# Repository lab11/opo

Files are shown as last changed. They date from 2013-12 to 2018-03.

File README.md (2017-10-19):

Opo
===

Opo is a face-to-face interaction sensor, able to characterize face to face interactions with 5~cm accuracy 
and 2~s temporal fidelity while maintaining a week-long battery life on a relatively small (110 mAh) battery.

Installation
---

1) Checkout my version of Contiki:

    git clone --recursive https://github.com/lab11/contiki.git
    git checkout cc2538-opo

2) Install a toolchain:
    Detailed instructions can be found at https://github.com/lab11/contiki/tree/cc2538-opo/platform/cc2538dk
    In ubuntu:
    sudo add-apt-repository ppa:terry.guo/gcc-arm-embedded
    sudo apt-get update
    sudo pat-get install gcc-arm-none-eabi 

3) Checkout the Opo repo
    git clone https://github.com/lab11/opo.git

4) Download Android studio 
    http://developer.android.com/sdk/index.html

5) Either make or ask us for a programmer
    https://github.com/lab11/epic-multi-prog.git

6) Either make or ask us for Opo boards
    opo/hardware/Opo8001v2 - No FTDI

7) If making your own boards, we recommend these batteries: https://www.sparkfun.com/products/13112

8) Go to /contiki/apps/opo8001v2opo_plugin in the Opo repo.

9) Modify line 9 (CONTIKI = /home/wwhuang/Dropbox/git/contiki) to point to whever you checked out my Contiki repo to (step 1). 

10) Connect the Opo to the programmer using a tag connect cable <http://www.tag-connect.com/TC2030-IDC-NL>. 

11) Install the opo89001v2opo_plugin app by typing python2 idmake ID in a terminal, where ID is a 16 bit unsigned integer 
that will be used as the targeted Opo's ID during ranging operations.

Usage
---

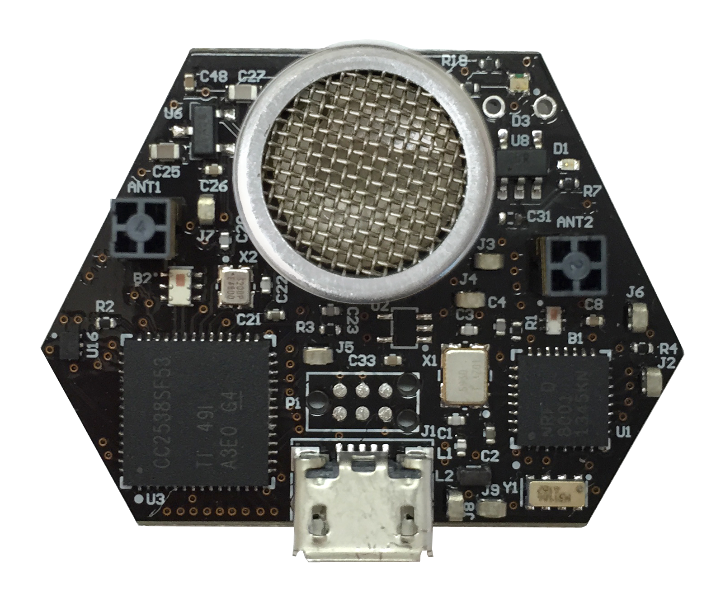
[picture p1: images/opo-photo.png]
Opo sensor


### Attaching Opos to people

We are currently working on a 3d printed case. In the meantime, obtain a lanyward, such as this one 
<https://www.amazon.com/MIFFLIN-Vertical-Badge-Holder-Lanyard/dp/B01G7VTE98/ref=sr_1_2?ie=UTF8&qid=1499377440&sr=8-2-spons&keywords=lanyard&psc=1&smid=A29P802DGSGI7W>.
Carve a hole in the plastic such that the transducer (large silver part with mesh) pokes out of the sheathe, and use 
electric tape to secure the Opo inside the sheathe if neccessary. 

The Opo must be worn such that they are unobstructed (e.g, NOT behind a shirt), and so that the transducer is facing 
forward. Ideally, the Opo should be worn near the neck, such that they are facing forward while not pointing upwards, 
as can happen on the chest.

### Charging the Opos and downloading the data

Opos can be charged from standard microUSB chargers, such as the ones used to charge smartphones. They can also 
be charged from laptops, or really anything that provides USB power. 

To download the data, one must plug in the Opo and then run the nodejs application, cloudcomm.js, found in the 
/node folder of the Opo repository. When the Opo is plugged in, the LED should turn blue, and when the Opo is uploading data the blue and red LEDs will blink. Keep in mind the LEDs are provided by one RGB LED, so if both the red and blue LEDs are on, the light will look purple. The data gets downloaded as JSON in a file titled opo_cc_data.dat. The key pieces of data are: 

* RX_ID: This Opo's ID 
* TX_ID: The other Opo's ID
* RANGE: distance between the two Opos in meters 
* M_UNIXTIME: This Opo's sense of what time the interaction occurred, expressed as a unix timestamp. 
* TX_UNIXTIME: The other Opo's sense of what time the interaction occurred, expressed as a unix timestamp.

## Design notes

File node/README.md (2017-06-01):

Cloudcomm
========

1. Install the most recent release of nodejs
	- https://nodejs.org/en/download/current/

2. Follow the Prerequisites section of Noble:
    - https://github.com/sandeepmistry/noble

3. Install some node packages:
    - npm install async
    - npm install request
    - npm install sleep
    - npm install noble@0.3.14
    - npm install fs

4. Run cloudcomm:
    - node cloudcomm.js

Currently, Cloudcomm is set up to append all data as JSON strings to opo_cc_data.csv.

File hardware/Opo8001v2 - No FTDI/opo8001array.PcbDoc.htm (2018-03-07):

Reporting Options

# File in Previous Format

Date | : | 8/17/2016
Time | : | 10:40:24 AM
Filename | : | C:\Users\wwhuang\Dropbox\git\opo\hardware\Opo8001v2 - No FTDI\opo8001array.PcbDoc

Version | Warning

This file was generated by an earlier version of the software

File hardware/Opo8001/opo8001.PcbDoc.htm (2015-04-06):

Reporting Options

# File in Previous Format

Date | : | 3/30/2015
Time | : | 3:05:40 PM
Filename | : | C:\Users\wwhuang\Dropbox\git\opo\hardware\Opo8001\opo8001.PcbDoc

Version | Warning

This file was generated by an earlier version of the software

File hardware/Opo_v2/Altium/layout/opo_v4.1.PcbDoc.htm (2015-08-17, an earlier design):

Reporting Options

# File in Previous Format

Date | : | 3/31/2015
Time | : | 12:49:01 PM
Filename | : | C:\Users\wwhuang\Dropbox\git\opo\hardware\Opo_v2\Altium\layout\opo_v4.1.PcbDoc

Version | Warning

This file was generated by an earlier version of the software

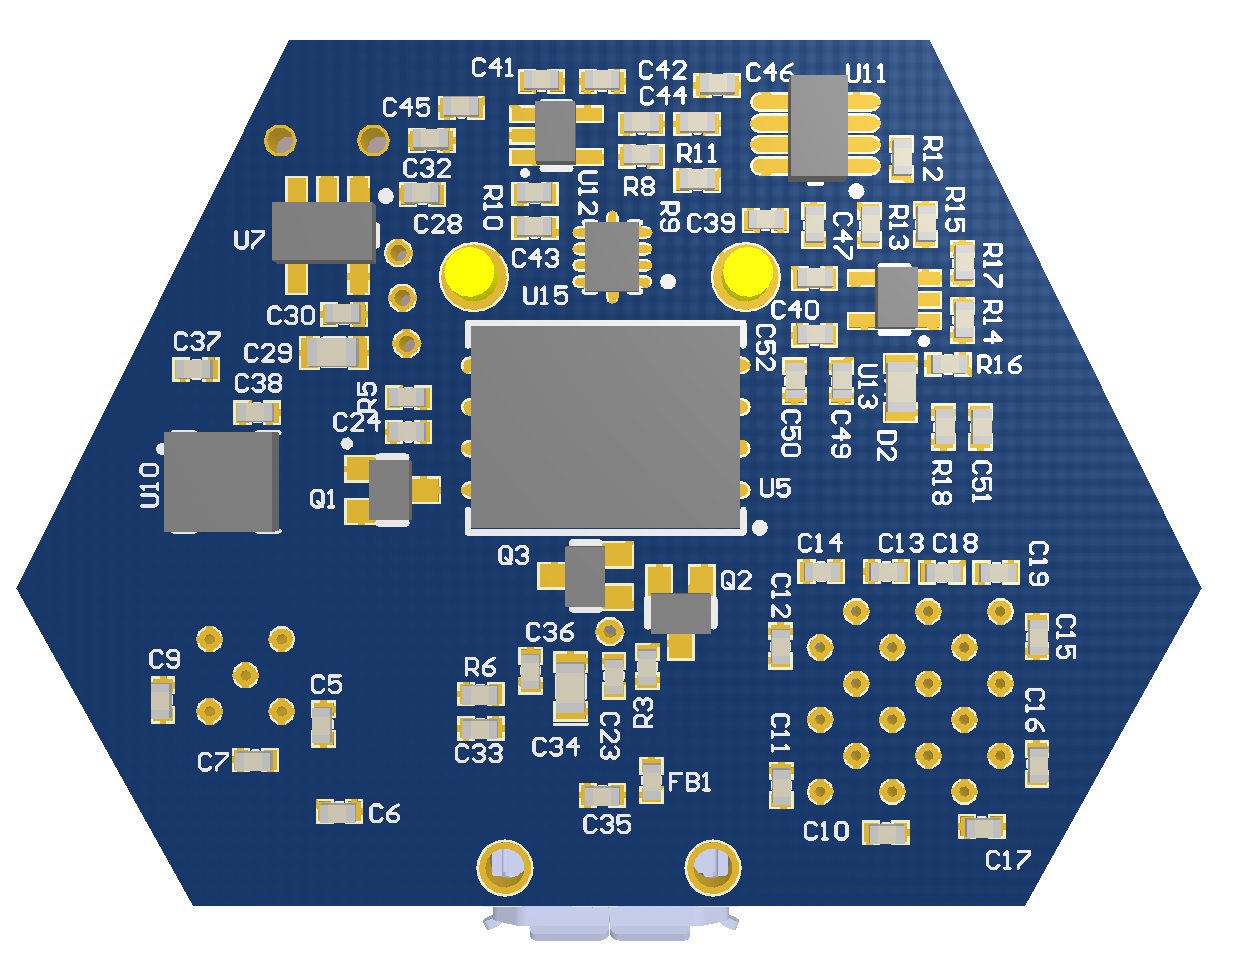
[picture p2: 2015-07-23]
hardware/Opo8001/opo8001-back.jpg

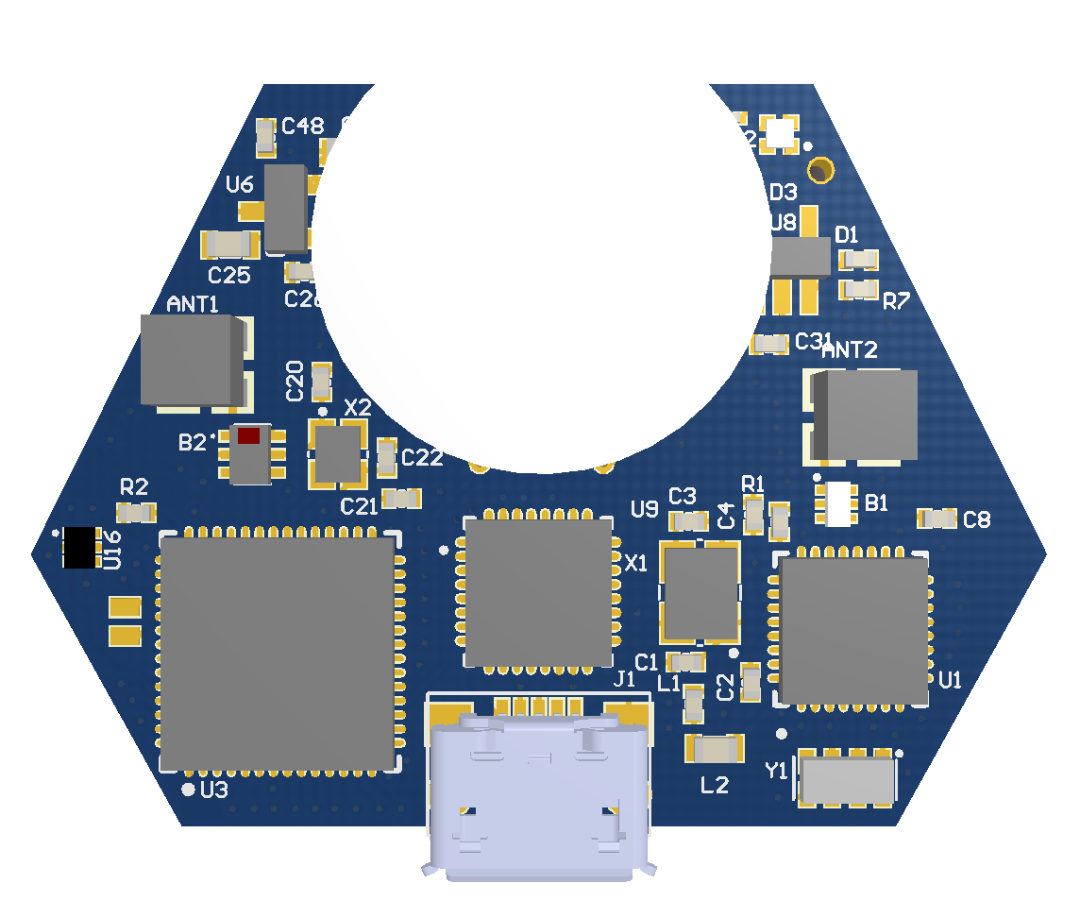
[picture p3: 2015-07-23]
hardware/Opo8001v2/opo8001-front.jpg

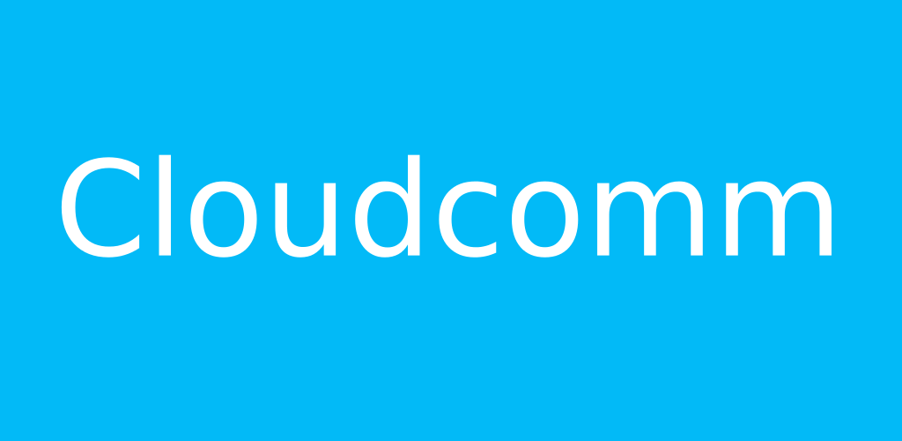
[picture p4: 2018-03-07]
android/Cloudcomm2/feature_image.png

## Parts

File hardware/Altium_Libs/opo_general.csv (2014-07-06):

LIBRARYREFERENCE | FOOTPRINT1 | FOOTPRINT2 | CAPACITY | COMMENT | DATASHEET | ESR | FREQUENCY | LOAD CAPATANCE | MANUFACTURER | MANUFACTURERPARTNO | MFR | MFR PART NUMBER | NOTE | STABILITY | SUPPLIER 1 | SUPPLIER 1 PART NUMBER | SUPPLIER 2 | SUPPLIER 2 PART NUMBER | SUPPLIER PART NUMBER 1 | VALUE | SHEETPART | DESIGNATOR | DESCRIPTION
ABS05 | ABS05 |  |  | ABS05 |  |  |  |  |  |  |  |  |  |  | Digi-Key |  |  |  | 535-11899-1-ND |  | * | Y? | 32768 Hz SMD Low profile crystal
ABS06-107-32.768KHZ-T |  |  |  | 32.768 kHz crystal |  |  |  |  |  |  | Abracon | ABS06-107-32.768KHZ-T |  |  | Digikey | 535-12373-1-ND |  |  |  | 32.768kHz | * | X? | 32.768 0805 SMD crystal
ADG849 | SC70-6 |  |  | ADG849 |  |  |  |  |  |  |  |  |  |  | Digi-Key |  |  |  | ADG849YKSZ500RLCT-ND |  | * | U? | 0.5 ? SPDT/2:1 Mux in SC70
ADP162 | TSOT23-5 |  |  | ADP162 |  |  |  |  |  |  |  |  |  |  | Digi-Key |  |  |  | ADP162AUJZ-3.3-R7CT-ND |  | * | U? | IC REG LDO 3.3V 0.15A TSOT23-5
ADXL362 | LGA_CC-16-4 |  |  | ADXL362 |  |  |  |  |  |  |  |  |  |  | Digi-Key |  |  |  | ADXL362BCCZ-RL7CT-ND |  | * | U? | Micropower, 3-Axis, ±2 g/±4 g/±8 g Digital Output MEMS Accelerometer
AS1976 | SOT23-5 |  |  | AS1976 |  |  |  |  |  |  |  |  |  |  | Digi-Key |  |  |  | AS1976-TCT-ND |  | * | U? | IC COMPARATOR PUSH/PULL SOT23-5
BD2425N50200AHF | BD2425N50200AHF |  |  | BD2425N50200AHF |  |  |  |  |  |  |  |  |  |  | Digi-Key |  |  |  | 1173-1063-1-ND |  | * | B? | Ultra Low Profile 0404 Balun 50? to 200? Balanced
BM02B-GHS-TBT | JST GH series |  |  | BM02B-GHS-TBT |  |  |  |  |  |  |  |  |  |  | Digi-Key |  |  |  | 455-1578-1-ND |  | * | J? | GH housing, 1.25 mm pitch, 2 positions
CC2420 | QFN50P700X700X100_HS-49N |  |  | CC2420 |  |  |  |  |  |  |  |  |  |  | Digi-Key |  |  |  | 296-19585-1-ND |  | * | U? | 2.4 GHz IEEE 802.15.4 / ZigBee-ready RF Transceiver
DMG1013UW | SC70-3 |  |  | DMG1013UW |  |  |  |  |  |  |  |  |  |  | Digi-Key |  |  |  | DMG1013UW-7DICT-ND |  | * | Q? | P-CHANNEL ENHANCEMENT MODE MOSFET
DS2411 | SOT23-3N |  |  | DS2411 |  |  |  |  |  |  |  |  |  |  | Digi-Key |  |  |  | DS2411R+CT-ND |  | * | U? | Silicon Serial Number with VCC Input
Ground Antenna | Chip Antenna |  |  | Ground Antenna |  |  |  |  |  |  |  |  |  |  | RichardsonRFPD |  |  |  | FR05-S1-N-0102B |  | * | ANT? | 2.4GHz Surface Mount Device (SMD) On Ground Antenna, 50 Ohms
IC_FT232RQ | QFN-32 |  |  | FT232RQ |  |  |  |  | * | * |  |  | * |  | Digi-Key |  |  |  | 768-1008-1-ND |  | * | U? | FT232R USB UART
ISL60002 | SOT23-3N |  |  | ISL60002 |  |  |  |  |  |  |  |  |  |  | Digi-Key |  |  |  | ISL60002DIH310Z-TKCT-ND |  | * | U? | IC VREF SERIES PREC SOT-23-3
MAX1555 | SOT23-5 |  |  | MAX1555 |  |  |  |  |  |  |  |  |  |  | Digi-Key |  |  |  | MAX1555EZK+TTR-ND |  | * | U? | 3 Dual-Input USB/AC Adapter 1-Cell Li+ Battery Chargers
MIC861 | SC70-5 |  |  | MIC861 |  |  |  |  |  |  |  |  |  |  | Digi-Key |  |  |  | 576-2932-1-ND |  | * | U? | IC OPAMP 400KHZ 2.7V ULT LP SC70
MIC863 | TSOP65P280X145-8N |  |  | MIC863 |  |  |  |  |  |  |  |  |  |  | Digi-Key |  |  |  | 576-2934-1-ND |  | * | U? | Dual Ultra Low Power Op Amp in SOT23-8
MSP430F1611 | QFN50P900X900X90_HS-65N |  |  | MSP430F1611 |  |  |  |  |  |  |  |  |  |  | Digi-Key |  |  |  | 296-18102-1-ND |  | * | U? | MIXED SIGNAL MICROCONTROLLER
Micro USB | Micro USB-B |  |  | micro USB-B |  |  |  |  |  |  |  |  |  |  | Digi-Key |  |  |  | 609-4616-6-ND |  | * | J? | CONN USB MICRO B RECPT SMT R/A
NLX2G14 | ULLGA6 |  |  | NLX2G14 |  |  |  |  |  |  |  |  |  |  | Digi-Key |  |  |  | NLX2G14AMX1TCGOSCT-ND |  | * | U? | IC INVERTER DUAL SCHMTRIG ULLGA6
NX3L4684 | QFN50P155X200X13-10N |  |  | NX3L4684 |  |  |  |  |  |  |  |  |  |  | Digi-Key |  |  |  | 568-5564-1-ND |  | * | U? | IC ANALOG SWITCH SPDT 10XQFN
RV-4162-C7 | RV4162 |  |  | RV-4162-C7 |  |  |  |  |  |  |  |  |  |  | Newark |  |  |  | 09X0517 |  | * | Y? | Real Time Clock Module with I2C Bus
SHT25 | DFN6 |  |  | Humidity and Temperature Sensor IC |  |  |  |  |  |  |  |  |  |  | Newark |  |  |  | 20T1173 |  | * | U? | SHT25
SM02B-SRSS-TB | JST SH series |  |  | SM02B-SRSS-TB |  |  |  |  |  |  |  |  |  |  | Digi-Key |  |  |  | 455-1802-1-ND |  | * | J? | CONN HEADER SH 2POS SIDE 1MM TIN
SN74AUP1G08 | SC70-5 |  |  | SN74AUP1G08 |  |  |  |  |  |  |  |  |  |  | Digi-Key |  |  |  | 296-19075-1-ND |  | * | U? | IC SNGL 2IN POS-AND GATE SC70-5
SST25VF032B | WSON |  |  | SST25VF032B |  |  |  |  |  |  |  |  |  |  | Digi-Key |  |  |  | SST25VF032B-80-4I-QAE-ND |  | * | U? | 32 Mbit SPI Serial Flash
SST25VF064C | WSON |  | 64 MBit | SST25VF064C |  |  |  |  |  |  |  |  |  |  | Digi-Key |  |  |  | SST25VF064C-80-4I-Q2AE-CT-ND |  | * | U? | 64 Mbit SPI Serial Dual I/O Flash
Si7021 | DFN6-Si7021 |  |  | Si7021 |  |  |  |  |  |  |  |  |  |  | Digikey |  |  |  | 336-2542-1-ND |  | * | U? | Temperature and Humidity Sensor
TS3A24159 | TSSOP50P490X110-10N |  |  | TS3A24159 |  |  |  |  |  |  |  |  |  |  | Digi-Key |  |  |  | 296-21913-1-ND |  | * | U? | DUAL-CHANNEL 2:1 MULTIPLEXER/DEMULTIPLEXER
TS881 | SC70-5 |  |  | TS881 |  |  |  |  |  |  |  |  |  |  | Digi-Key |  |  |  | 497-13217-1-ND |  | * | U? | Rail-to-rail 1.1 V nanopower comparator
TS882 | SO8 |  |  | TS882 |  |  |  |  |  |  |  |  |  |  | Digikey | 497-14073-1-ND | Digikey | 497-13800-1-ND |  |  | * | U? | Ultra Low Power Dual Comparator
TSX-3225 | TSX-3225 |  |  | 16MHz Crystal |  |  |  |  |  |  | Epson | TSX-3225 16.0000MF09Z-AC3 |  |  | Digikey | SER3628CT-ND |  |  |  | 16MHz | * | Y? | 3.2x2.5mm 16MHz SMD crystal
TXC 7B | TXC 7B |  |  | TXC 7B |  | 40 | 16 MHz | 18 pF |  |  |  |  |  | 30 ppm | Digi-Key |  |  |  | 887-1104-1-ND |  | * | Y? | 5 x 3.2 mm SMD SEAM CRYSTAL 7B SERIES
TestPoint | TestPoint | TestPoint |  | 5004 | http://mail.keyelco.com/ENG._DEPT/PDF%20CAT%20NO%20Drawings/5004.pdf |  |  |  |  |  |  |  |  |  | Digi-Key |  |  |  | 5004K-ND |  | * | J? | TEST POINT PC MINI .040D YELLOW"
Tranducer | Transducer recepticle |  |  | 400EP250 |  |  |  |  |  |  |  |  |  |  | Digi-Key |  |  |  | ED90088-ND |  | * | UT? | Air Ultrasounic Ceramic Transducers
ZXM61P03 | SOT23-3N |  |  | ZXM61P03 |  |  |  |  |  |  |  |  |  |  | Digi-Key |  |  |  | ZXM61P03FCT-ND |  | * | Q? | 30V P-CHANNEL ENHANCEMENT MODE MOSFET
cc2538 | QFN50P800X800X100_HS-57N |  |  | cc2538 |  |  |  |  |  |  |  |  |  |  |  |  |  |  |  |  | * | U? | cc2538 MCU/802.15.4 radio
cc2538_Balun | Chip Balun |  |  | BALUN |  |  |  |  |  |  |  |  |  |  | Digikey |  |  |  | 712-1536-1-ND |  | * | U? | Johanson CC253X Balun
nrf8001 | QFN50P500X500X90_HS-33N |  |  | nrf8001 |  |  |  |  |  |  |  |  |  |  | Digikey | 1490-1026-ND |  |  |  |  | * | U? | nrf8001 Bluetooth SPI module
nrf8001_balun | 2450BM14A0002 |  |  | 2450BM14A0002 |  |  |  |  |  |  | Johanson | 2450BM14A0002 |  |  | Digikey | 712-1574-1-ND |  |  |  |  | * | B? | nrf8001 chip balun

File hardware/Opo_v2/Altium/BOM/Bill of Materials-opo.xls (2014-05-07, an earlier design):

Designator | Description | Value | Footprint | Quantity | Supplier 1 | Supplier Part Number 1
ANT1 | 2.4GHz Surface Mount Device (SMD) On Ground Antenna, 50 Ohms |  | Chip Antenna | 1.0 | Digi-Key | WM4893CT-ND
B1 | Ultra Low Profile 0404 Balun 50? to 200? Balanced |  | BD2425N50200AHF | 1.0 | Digi-Key | 1173-1063-1-ND
C1, C2, C3, C4, C5, C6, C7, C9, C10, C11, C12, C13, C14, C15, C16, C17, C18, C21, C23, C25, C33, C34, C35, C39, C40, C42, C43, C44, C45, C46 | Ceramic capacitor, 0.1u, 0402 package | 0.1 uF | 0402 | 30.0 | Digi-Key | 445-1265-1-ND
C8 | Tantalum capacitor, 10 uF, 0603 package | 10 uF | 0603 - Polar Marking | 1.0 | Digi-Key | 478-4959-1-ND
C19, C20 | Ceramic capacitor, 30 pF, 0402 package | 30 pF | 0402 | 2.0 | Digi-Key | 712-1295-1-ND
C22 | Ceramic capacitor, 12 pF, 0402 package | 12 pF | 0402 | 1.0 | Digi-Key | 712-1256-1-ND
C24, C26, C28, C41 | Ceramic capacitor, 10 uF, 0603 package | 10 uF | 0603 | 4.0 | Digi-Key | 445-4112-1-ND
C27, C29, C30, C31, C37 | Ceramic capacitor, 1 uF, 0402 package | 1 uF | 0402 | 5.0 | Digi-Key | 445-5000-1-ND
C32 | Tantalum capacitor, 4.7 uF, 0603 package | 4.7 uF | 0603 - Polar Marking | 1.0 | Digi-Key | 511-1496-1-ND
C36, C38 | Ceramic capacitor, 47 pF, 0402 package | 47 pF | 0402 | 2.0 | Digi-Key | 709-1121-1-ND
C47 | Ceramic capacitor, 1000 pF, 0402 package | 1000 pF | 0402 | 1.0 | Digi-Key | 445-6846-1-ND
D1 | LED, Green, 0402 |  | 0402 - DIODE | 1.0 | Digi-Key | 511-1592-1-ND
D2 | LED, Red, 0402 |  | 0402 - DIODE | 1.0 | Digi-Key | 511-1593-1-ND
D3 | LED, Orange, 0402 |  | 0402 - DIODE | 1.0 | Digi-Key | 511-1590-1-ND
D4 | Schottky diode 30 V 0.1 A 0603 |  | 0603 - DIODE | 1.0 | Digi-Key | 641-1282-1-ND
FB1, FB2, FB3 | Ferrite Bead, 150 mA, 0402 package |  | 0402 | 3.0 | Digi-Key | 587-1835-1-ND
J1 | CONN HEADER SH 2POS SIDE 1MM TIN |  | JST SH series | 1.0 | Digi-Key | 455-1802-1-ND
J2 | CONN USB MICRO B RECPT SMT R/A |  | Micro USB-B | 1.0 | Digi-Key | 609-4616-6-ND
L1 | Chip inductor, 6.8 nH, 0402 package | 6.8 nH | 0402 | 1.0 | Digi-Key | 712-1419-1-ND
Q1 | P-CHANNEL ENHANCEMENT MODE MOSFET |  | SC70-3 | 1.0 | Digi-Key | DMG1013UW-7DICT-ND
R1, R2 | Chip resistor, 10K, 0402 package | 10K | 0402 | 2.0 | Digi-Key | 541-10.0KLDKR-ND
R3, R4, R10, R12, R13, R14, R17, R19, R21 | Chip resistor, 100K, 0402 package | 100K | 0402 | 9.0 | Digi-Key | 541-100KLCT-ND
R5 | Chip resistor, 43K, 0402 package | 43K | 0402 | 1.0 | Digi-Key | 541-43.0KLCT-ND
R6, R7 | Chip resistor, 470, 0402 package | 470 | 0402 | 2.0 | Digi-Key | 541-470LCT-ND
R8 | Chip resistor, 0, 0402 package | 0 | 0402 | 1.0 | Digi-Key | 541-0.0YBCT-ND
R9, R16, R18, R20 | Chip resistor, 1M, 0402 package | 1M | 0402 | 4.0 | Digi-Key | 541-1.00MLCT-ND
R11 | Chip resistor, 2.2K, 0402 package | 2.2K | 0402 | 1.0 | Digi-Key | 541-2.20KLCT-ND
R15 | Chip resistor, 1K, 0402 package | 1K | 0402 | 1.0 | Digi-Key | 541-1.00KLCT-ND
R22 | Chip resistor, 1.24M, 0402 package | 1.24M | 0402 | 1.0 | Digi-Key | 541-1.24MLCT-ND
R23 | Chip resistor, 37.4K, 0402 package | 37.4K | 0402 | 1.0 | Digi-Key | 541-37.4KLCT-ND
R24 | Chip resistor, 27K, 0402 package | 27K | 0402 | 1.0 | Digi-Key | 541-27.0KLCT-ND
R25 | Chip resistor, 422K, 0402 package | 422K | 0402 | 1.0 | Digi-Key | 541-422KLCT-ND
R26 | Chip resistor, 270K, 0402 package | 270K | 0402 | 1.0 | Digi-Key | 541-270KLCT-ND
U1 | Micropower, 3-Axis, ±2 g/±4 g/±8 g Digital Output MEMS Accelerometer |  | LGA_CC-16-4 | 1.0 | Digi-Key | ADXL362BCCZ-RL7CT-ND
U2 | Temperature and Humidity Sensor |  | DFN6-Si7021 | 1.0 | Digikey | 336-2542-1-ND
U3 | 2.4 GHz IEEE 802.15.4 / ZigBee-ready RF Transceiver |  | QFN50P700X700X100_HS-49N | 1.0 | Digi-Key | 296-19585-1-ND
U4 | MIXED SIGNAL MICROCONTROLLER |  | QFN50P900X900X90_HS-65N | 1.0 | Digi-Key | 296-18102-1-ND
U5, U16 | IC ANALOG SWITCH SPDT 10XQFN |  | QFN50P155X200X13-10N | 2.0 | Digi-Key | 568-5564-1-ND
U6 | Silicon Serial Number with VCC Input |  | SOT23-3N | 1.0 | Digi-Key | DS2411R+CT-ND
U7 | 64 Mbit SPI Serial Dual I/O Flash |  | WSON | 1.0 | Digi-Key | SST25VF064C-80-4I-Q2AE-CT-ND
U8 | IC VREF SERIES PREC SOT-23-3 |  | SOT23-3N | 1.0 | Digi-Key | ISL60002DIH310Z-TKCT-ND
U9 | Ultralow Quiescent Current, 150 mA, CMOS Linear Regulators |  | TSOT23-5 | 1.0 | Digi-Key | ADP162AUJZ-3.3-R7CT-ND
U10 | 3 Dual-Input USB/AC Adapter 1-Cell Li+ Battery Chargers |  | SOT23-5 | 1.0 | Digi-Key | MAX1555EZK+TTR-ND
U11 | FT232R USB UART |  | QFN-32 | 1.0 | Digi-Key | 768-1008-1-ND
U12 | IC OPAMP 400KHZ 2.7V ULT LP SC70 |  | SC70-5 | 1.0 | Digi-Key | 576-2932-1-ND
U13 | Dual Ultra Low Power Op Amp in SOT23-8 |  | TSOP65P280X145-8N | 1.0 | Digi-Key | 576-2934-1-ND
U14 | 0.5 ? SPDT/2:1 Mux in SC70 |  | SC70-6 | 1.0 | Digi-Key | ADG849YKSZ500RLCT-ND
U15 | Rail-to-rail 1.1 V nanopower comparator |  | SC70-5 | 1.0 | Digi-Key | 497-13217-1-ND
U17 | Dual Schmitt-Trigger Inverter |  | ULLGA6 | 1.0 | Digi-Key | NLX2G14AMX1TCGOSCT-ND
UT1 | Air Ultrasounic Ceramic Transducers |  | Transducer recepticle | 1.0 | Digi-Key | ED90088-ND
Y1 | Real Time Clock Module with I2C Bus |  | RV4162 | 1.0 | Newark | 09X0517
Y2 | 5 x 3.2 mm SMD SEAM CRYSTAL 7B SERIES |  | TXC 7B | 1.0 | Digi-Key | 887-1104-1-ND

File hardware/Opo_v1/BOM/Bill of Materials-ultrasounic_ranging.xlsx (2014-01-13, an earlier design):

Designator | Description | Footprint | Quantity | Supplier Part Number 1 | Supplier Part Number 2 | Value
ANT1 |  | Inverted F Antenna | 1
C1, C3, C10, C11, C12, C13, C15, C16, C18, C19, C20 | Capacitor (Semiconductor SIM Model) | 1608[0603] | 11 |  |  | 0.1uF
C2, C4, C21, C22 | Capacitor (Semiconductor SIM Model) | 1608[0603] | 4 |  |  | 10uF
C5, C6, C9 | Capacitor (Semiconductor SIM Model) | 1608[0603] | 3 |  |  | 1uF
C7, C8, C14 | Capacitor (Semiconductor SIM Model) | 1608[0603] | 3 |  |  | 4pF
C17 | Capacitor (Semiconductor SIM Model) | 1608[0603] | 1 |  |  | 10nF
C23, C24 | Capacitor (Semiconductor SIM Model) | 1608[0603] | 2 |  |  | 47pF
D1, D2 | Typical BLUE SiC LED | J1-0603 | 2
D3 | Default Diode | J1-0603 | 1
J1 |  | Micro USB | 1 | 732-2018-2-ND | 609-4616-2-ND
J3, J6 | TEST POINT PC MINI .040"D YELLOW | TestPoint | 2 | 5004K-ND
J4, J5 | PIN RECEPTACLES | 0360 SER | 2 | ED90088-ND
P1 | 100 mils standard header | 1x2 header | 1 | 3M9447-ND
Q1 | 30V P-CHANNEL ENHANCEMENT MODE MOSFET | SOT23-3N | 1 | ZXM61P03FCT-ND
R1, R2 | Resistor | J1-0603 | 2 |  |  | 10K
R3, R4 | Resistor | J1-0603 | 2 |  |  | 470
R5, R6, R9, R14 | Resistor | J1-0603 | 4 |  |  | 1Meg
R7, R8, R10 | Resistor | J1-0603 | 3 |  |  | 100K
R11, R13 | Resistor | J1-0603 | 2 |  |  | 2k
R12 | Resistor | J1-0603 | 1 |  |  | 1.24M
R15 | Resistor | J1-0603 | 1 |  |  | 422K
R18 | Resistor | J1-0603 | 1 |  |  | 100Meg
R19, R20, R21 | Resistor | J1-0603 | 3 |  |  | 0
R22 | Resistor | J1-0603 | 1 |  |  | 37.4K
SW1 | Switch | EVQP2 | 1 | P12298SCT-ND
SW2 | Switch 3 Pos | Slide Switch SPDT | 1 | EG1903-ND | 450-1598-ND
U1 | EPIC Core | EPIC_LCC68 | 1
U2 | Precision Low Power FGA? Voltage References | SOT23-3N | 1 | ISL60002DIH310Z-TKCT-ND
U3 | Ultralow Quiescent Current, 150 mA, CMOS Linear Regulators | TSOT23-5 | 1 | ADP162AUJZ-3.3-R7CT-ND
U4 | DUAL-CHANNEL 2:1 MULTIPLEXER/DEMULTIPLEXER | TSSOP50P490X110-10N | 1 | 296-21913-1-ND
U5, U6, U7 | Teeny, Ultra Low Power Op Amp | SC70-6 | 3 | 576-2932-1-ND
U8 | Ultra-Low Current, 1.8V Comparators | SOT23-5 | 1 | AS1976-TCT-ND
U9 | Dual Schmitt-Trigger Inverter | ULLGA6 | 1 | NLX2G14AMX1TCGOSCT-ND
U10 | LOW-POWER SINGLE 2-INPUT POSITIVE-AND GATE | SC70-6 | 1 | 296-19074-1-ND
U11 | MEMS digital output motion sensor | LGA-16 | 1 | 497-10613-6-ND
UT1 | Air Ultrasounic Ceramic Transducers | Transducer | 1 | 98K9162
Y1 | Real Time Clock Module with I2C Bus | RV4162 | 1 | R1033504

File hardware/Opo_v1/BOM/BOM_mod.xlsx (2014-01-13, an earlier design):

Designator | Description | Footprint | Quantity | Mfg. Part No. | Supplier Part Number 1 | Value | Note
C1, C3, C10, C11, C12, C13, C15, C16, C18, C19, C20 | Capacitor | 0603 | 11 |  | 445-1316-1-ND | 0.1uF
C2, C4, C21, C22 | Capacitor | 0603 | 4 |  | 445-4112-1-ND | 10uF
C5, C6, C9 | Capacitor | 0603 | 3 |  | 445-1322-1-ND | 1uF
C7, C8, C14 | Capacitor | 0603 | 3 |  |  | 4pF | DNI
C17 | Capacitor | 0603 | 1 | C0603C102K3RACTU | 399-7834-1-ND | 1nF
C23, C24 | Capacitor | 0603 | 2 |  | 445-1277-1-ND | 47pF
D1 | LED | 0603 | 1 | TLMG1100-GS08 | 751-1165-1-ND
D2 | LED | 0603 | 1 |  | 475-2816-1-ND
D3 | Diode | 0603 | 1 |  | 641-1282-1-ND
J1 | Micro USB |  | 1 |  | 609-4616-2-ND
J3, J6 | Test Point | TestPoint | 2 |  | 5004K-ND
J4, J5 | PIN RECEPTACLES |  | 2 |  | ED90088-ND
P1 | 100 mils standard header | 1x2 header | 1 |  | 3M9447-ND
Q1 | PFET | SOT23-3N | 1 |  | ZXM61P03FCT-ND
R1, R2 | Resistor | 0603 | 2 |  | A102203CT-ND | 10K
R3, R4 | Resistor | 0603 | 2 |  | 541-470GCT-ND | 470
R5, R6, R9 | Resistor | 0603 | 4 |  | 311-1.00MHRCT-ND | 1Meg
R14 | Resistor | 0603 | 1 | ERJ-3EKF2703V | P270KHCT-ND | 270k
R7, R8, R10 | Resistor | 0603 | 3 |  | A106046CT-ND | 100K
R11 | Resistor | 0603 | 1 |  | P2.0KGCT-ND | 2k | DNI
R13 | Resistor | 0603 | 1 | ERJ-3EKF2702V | P27.0KHCT-ND | 27k
R12 | Resistor | 0603 | 1 |  | 541-1.24MHCT-ND | 1.24M
R15 | Resistor | 0603 | 1 |  | 311-422KHRCT-ND | 422K
R18 | Resistor | 0603 | 1 |  |  | 100Meg | DNI
R20, R21 | Resistor | 0603 | 3 |  |  | 0 | DNI
R19 | Resistor | 0603 | 1 | ERJ-3GEY0R00V | P0.0GCT-ND | 0
R22 | Resistor | 0603 | 1 |  | 541-37.4KHCT-ND | 37.4K
SW1 | Switch |  | 1 |  | P12298SCT-ND
SW2 | Switch 3 Pos |  | 1 |  | 450-1577-ND
U1 | EPIC Core |  | 1
U2 | Precision reference | SOT23-3N | 1 |  | ISL60002DIH310Z-TKCT-ND | 1.25V
U3 | Linear Regulators | TSOT23-5 | 1 |  | ADP162AUJZ-3.3-R7CT-ND | 150mA
U4 | Analog multiplexor | DGS | 1 |  | 296-21913-1-ND
U5, U6, U7 | Op Amp | SC70-6 | 3 |  | 576-2932-1-ND
U8 | Comparator | SOT23-5 | 1 |  | AS1976-TCT-ND
U9 | Dual inverter | ULLGA6 | 1 |  | NLX2G14AMX1TCGOSCT-ND
U10 | AND gate | SC70-6 | 1 |  | 296-19075-6-ND
U11 | Accelerometer | LGA-16 | 1 |  | 497-10613-6-ND
UT1 | Ultrasonic transducer |  | 1 | 98K9162
Y1 | RTC |  | 1 | RV-4162-C7

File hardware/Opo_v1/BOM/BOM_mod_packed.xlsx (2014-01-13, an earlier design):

Designator | Description | Footprint | Quantity | Supplier Part Number 1 | Value | Note
C1, C3, C10, C11, C12, C13, C15, C16, C18, C19, C20 | Capacitor | 603 | 11 | 445-1316-1-ND | 0.1uF |  | x
C2, C4, C21, C22 | Capacitor | 603 | 4 | 445-4112-1-ND | 10uF |  | x
C5, C6, C9 | Capacitor | 603 | 3 | 445-1322-1-ND | 1uF |  | x
C7, C8, C14 | Capacitor | 603 | 3 |  | 4pF | DNI
C17 | Capacitor | 603 | 1 |  | 10nF | DNI
C23, C24 | Capacitor | 603 | 2 | 609-4616-2-ND | 47pF |  | x
D1 | LED | 603 | 1 | 475-1410-1-ND |  |  | x
D2 | LED | 603 | 1 | 475-2816-1-ND |  |  | x
D3 | Diode | 603 | 1 | 641-1282-1-ND |  |  | x
J1 | Micro USB |  | 1 | 609-4616-2-ND |  |  | x
J3, J6 | Test Point | TestPoint | 2 | 5004K-ND |  |  | x
J4, J5 | PIN RECEPTACLES |  | 2 | ED90088-ND |  |  | x
P1 | 100 mils standard header | 1x2 header | 1 | 3M9447-ND |  |  | x
Q1 | PFET | SOT23-3N | 1 | ZXM61P03FCT-ND |  |  | x
R1, R2 | Resistor | 603 | 2 | A102203CT-ND | 10K |  | x
R3, R4 | Resistor | 603 | 2 | 541-470GCT-ND | 470 |  | x
R5, R6, R9 | Resistor | 603 | 4 | 311-1.00MHRCT-ND | 1Meg |  | x
R14 | Resistor | 603 | 1 | 311-1.00MHRCT-ND | 1Meg | DNI
R7, R8, R10 | Resistor | 603 | 3 | A106046CT-ND | 100K |  | x
R11, R13 | Resistor | 603 | 2 | P2.0KGCT-ND | 2k | DNI
R12 | Resistor | 603 | 1 | 541-1.24MHCT-ND |  |  | x
R15 | Resistor | 603 | 1 | 311-422KHRCT-ND | 422K |  | x
R18 | Resistor | 603 | 1 |  | 100Meg | DNI
R19, R20, R21 | Resistor | 603 | 3 |  | 0 | DNI
R22 | Resistor | 603 | 1 | 541-37.4KHCT-ND | 37.4K |  | x
SW1 | Switch |  | 1 | P12298SCT-ND |  |  | x
SW2 | Switch 3 Pos |  | 1 | 450-1577-ND |  |  | x
U1 | EPIC Core |  | 1
U2 | Precision reference | SOT23-3N | 1 | ISL60002DIH310Z-TKCT-ND | 1.25V |  | x
U3 | Linear Regulators | TSOT23-5 | 1 | ADP162AUJZ-3.3-R7CT-ND | 150mA |  | x
U4 | Analog multiplexor | DGS | 1 | 296-21913-1-ND |  |  | x
U5, U6, U7 | Op Amp | SC70-6 | 3 | 576-2932-1-ND |  |  | x
U8 | Comparator | SOT23-5 | 1 | AS1976-TCT-ND |  |  | x
U9 | Dual inverter | ULLGA6 | 1 | NLX2G14AMX1TCGOSCT-ND |  |  | x
U10 | AND gate | SC70-6 | 1 | 296-19074-1-ND |  |  | x
U11 | Accelerometer | LGA-16 | 1 | 497-10613-6-ND |  |  | x
UT1 | Ultrasonic transducer |  | 1 | 98K9162
Y1 | RTC |  | 1 | R1033504 |  |  | x

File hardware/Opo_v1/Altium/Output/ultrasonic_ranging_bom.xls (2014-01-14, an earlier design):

Comment | Description | Designator | Footprint | LibRef | Quantity
2.4GHz PCB Antenna |  | ANT1 | Inverted F Antenna | 2.4GHz PCB Antenna | 1.0
Cap Semi | Capacitor (Semiconductor SIM Model) | C1, C2, C3, C4, C5, C6, C7, C8, C9, C10, C11, C12, C13, C14, C15, C16, C17, C18, C19, C20, C21, C22, C23, C24 | 1608[0603] | Cap Semi | 24.0
LED3 | Typical BLUE SiC LED | D1, D2 | J1-0603 | LED3 | 2.0
Diode | Default Diode | D3 | J1-0603 | Diode | 1.0
6 pin connector |  | J1 | Micro USB | 6 pin connector | 1.0
5004 | TEST POINT PC MINI .040"D YELLOW | J3, J6 | TestPoint | TestPoint | 2.0
1 x 2 header | 100 mils standard header | P1 | 1x2 header | 1 x 2 header | 1.0
ZXM61P03 | 30V P-CHANNEL ENHANCEMENT MODE MOSFET | Q1 | SOT23-3N | ZXM61P03 | 1.0
10K | Resistor | R1, R2 | J1-0603 | Res3 | 2.0
470 | Resistor | R3, R4 | J1-0603 | Res3 | 2.0
1Meg | Resistor | R5, R6, R9 | J1-0603 | Res3 | 3.0
100K | Resistor | R7, R8, R10 | J1-0603 | Res3 | 3.0
2k | Resistor | R11 | J1-0603 | Res3 | 1.0
1.24M | Resistor | R12 | J1-0603 | Res3 | 1.0
27K | Resistor | R13, R22 | J1-0603 | Res3 | 2.0
270K | Resistor | R14 | J1-0603 | Res3 | 1.0
422K | Resistor | R15 | J1-0603 | Res3 | 1.0
Res3 | Resistor | R18, R19, R20, R21 | J1-0603 | Res3 | 4.0
EVQP2 | Switch | SW1 | EVQP2 | EVQP2 | 1.0
EG1218 | Switch 3 Pos | SW2 | Slide Switch SPDT | EG1218 | 1.0
EPIC_COREA | EPIC Core | U1 | EPIC_LCC68 | EPIC_COREA | 1.0
ISL60002 | Precision Low Power FGA? Voltage References | U2 | SOT23-3N | ISL60002 | 1.0
ADP162 | Ultralow Quiescent Current, 150 mA, CMOS Linear Regulators | U3 | TSOT23-5 | ADP162 | 1.0
TS3A24159 | DUAL-CHANNEL 2:1 MULTIPLEXER/DEMULTIPLEXER | U4 | TSSOP50P490X110-10N | TS3A24159 | 1.0
MIC861 | Teeny, Ultra Low Power Op Amp | U5, U6, U7 | SC70-6 | MIC861 | 3.0
AS1976 | Ultra-Low Current, 1.8V Comparators | U8 | SOT23-5 | AS1976 | 1.0
NLX2G14 | Dual Schmitt-Trigger Inverter | U9 | ULLGA6 | NLX2G14 | 1.0
SN74AUP1G08 | LOW-POWER SINGLE 2-INPUT POSITIVE-AND GATE | U10 | SC70-6 | SN74AUP1G08 | 1.0
LIS3DHTR | MEMS digital output motion sensor | U11 | LGA-16 | LIS3DHTR | 1.0
400EP250 | Air Ultrasounic Ceramic Transducers | UT1 | Transducer recepticle | Tranducer | 1.0
RV-4162-C7 | Real Time Clock Module with I2C Bus | Y1 | RV4162 | RV-4162-C7 | 1.0

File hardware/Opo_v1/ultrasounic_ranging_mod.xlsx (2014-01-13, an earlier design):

Designator | Description | Footprint | Quantity | Supplier Part Number 1 | Value | Note
C1, C3, C10, C11, C12, C13, C15, C16, C18, C19, C20 | Capacitor (Semiconductor SIM Model) | 0603 | 11 | 445-1316-1-ND | 0.1uF
C2, C4, C21, C22 | Capacitor (Semiconductor SIM Model) | 0603 | 4 | 445-4112-1-ND | 10uF
C5, C6, C9 | Capacitor (Semiconductor SIM Model) | 0603 | 3 | 445-1322-1-ND | 1uF
C7, C8, C14 | Capacitor (Semiconductor SIM Model) | 0603 | 3 |  | 4pF | DNI
C17 | Capacitor (Semiconductor SIM Model) | 0603 | 1 |  | 10nF | DNI
D1 | LED | 0603 | 1 | 475-1410-1-ND
D2 | LED | 0603 | 1 | 475-2816-1-ND
D3 | Diode | 0603 | 1 | 641-1282-1-ND
J1 | Micro USB |  | 1 | 609-4616-2-ND
J3, J6 | TEST POINT PC MINI .040"D YELLOW |  | 2 | 5004K-ND
J4, J5 | PIN RECEPTACLES |  | 2 | ED90088-ND
P1 | 100 mils standard header |  | 1 | 3M9447-ND
Q1 | 30V P-CHANNEL ENHANCEMENT MODE MOSFET | SOT23 | 1 | ZXM61P03FCT-ND
R1, R2 | Resistor | 0603 | 2 | A102203CT-ND | 10K
R3, R4 | Resistor | 0603 | 2 | 541-470GCT-ND | 470
R5, R6, R9, R14, R16, R17 | Resistor | 0603 | 6 | 311-1.00MHRCT-ND | 1Meg
R7, R8, R10 | Resistor | 0603 | 3 | A106046CT-ND | 100K
R11, R13 | Resistor | 0603 | 2 | P2.0KGCT-ND | 2k
R12, R15 | Resistor | 0603 | 2 |  | 0 | DNI
R18 | Resistor | 0603 | 1 |  | 100M | DNI
SW1 | Switch | EVQP2 | 1 | P12298SCT-ND
SW2 | Switch 3 Pos |  | 1 | 450-1598-ND
U1 | EPIC Core |  | 1
U2 | Precision Low Power FGA? Voltage References | SOT23 | 1 | ISL60002DIH310Z-TKCT-ND
U3 | Ultralow Quiescent Current, 150 mA, CMOS Linear Regulators | TSOT | 1 | ADP162AUJZ-3.3-R7CT-ND
U4 | DUAL-CHANNEL 2:1 MULTIPLEXER/DEMULTIPLEXER | DGS | 1 | 296-21913-1-ND
U5, U6, U7 | Teeny, Ultra Low Power Op Amp | SC70-6 | 3 | 576-2932-1-ND
U8 | Ultra-Low Current, 1.8V Comparators | SOT23-5 | 1 | AS1976-TCT-ND
U9 | Dual Schmitt-Trigger Inverter | ULLGA6 | 1 | NLX2G14AMX1TCGOSCT-ND
U10 | LOW-POWER SINGLE 2-INPUT POSITIVE-AND GATE | SC70-6 | 1 | 296-19074-1-ND
U11 | MEMS digital output motion sensor | LGA-16 | 1 | 497-10613-6-ND
UT1 | Air Ultrasounic Ceramic Transducers |  | 1 | 98K9162
Y1 | Real Time Clock Module with I2C Bus |  | 1 | J3

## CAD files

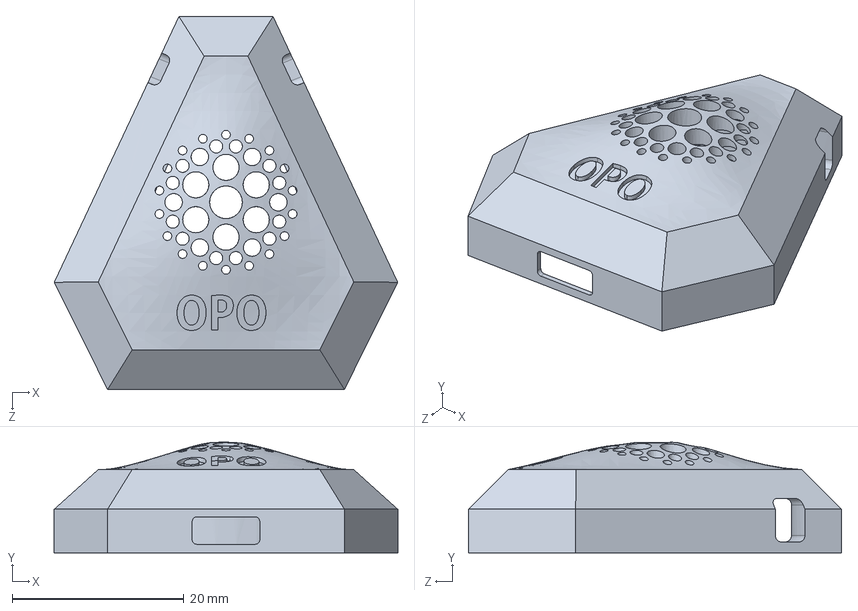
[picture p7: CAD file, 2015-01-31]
case/case_top_2.SLDPRT
40.0 x 12.9 x 43.4 mm

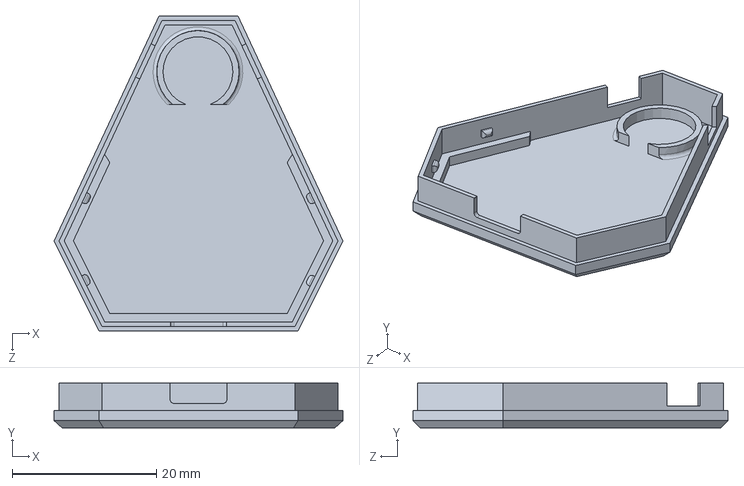
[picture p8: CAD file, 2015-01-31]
case/case_bottom.SLDPRT
40.1 x 6.22 x 43.7 mm

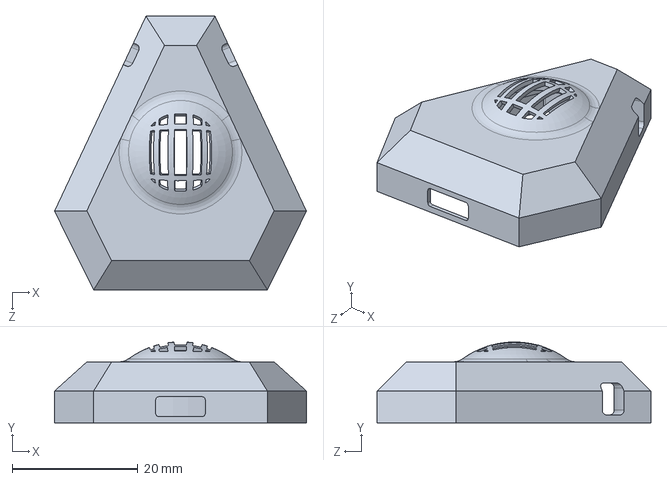
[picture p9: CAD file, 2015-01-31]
case/case_top.SLDPRT
40.0 x 12.9 x 43.4 mm

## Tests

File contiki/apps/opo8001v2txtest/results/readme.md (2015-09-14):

CH3: Ultrasonic output
CH2: current draw

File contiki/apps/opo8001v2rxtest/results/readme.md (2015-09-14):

CHA2 = Current (divide voltage by 50)
CHA3 = Opo RX comparator output

Range = 58.5 cm

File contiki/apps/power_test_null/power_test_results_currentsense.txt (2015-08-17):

No systick, explicit drop to LPM2 = 7 mA
No systick, no explicit drop LPM2 = 25 mA
No systick, sleep nrf8001, explicit drop to LPM2 = 192 uA

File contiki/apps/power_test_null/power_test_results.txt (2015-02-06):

Without systick interrupts: 41 uA @ 3.7 V = 151.7 uW sleep power draw
Without systick interrupts, without rv4162 clkout = 32 uA @ 3.7 V
With systick interrupts:  96 uA @ 3.7 V = 355.2 uW sleep power draw

40 mAh 3.7 V battery = 532,800 mJ

1 week desired lifetime:
Without systick interrupts: 91,748.16 mJ
With systick interrupts: 214,824.96 mJ

Measurements taken with a Fluke 189

Expected sleep current draw:
2 uA  -  cc2538 @ LPM2
4.2 uA - mic861
7 uA -   mic863
10 uA -  rv4162 w/ clkout
2 uA -   NC7WZ14L6x (comparator)
4 uA -   uPG2214TB (rf switch)
1 uA -   NC7S14P5x (inverter for rf switch)

.5 uA -  nrf8001
.35 uA - ISL6002
.41 uA - TS881 x 2
.01 uA - ADXL362

~33 uA - Sleep current

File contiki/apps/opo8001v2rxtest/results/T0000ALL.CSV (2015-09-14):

Model | MSO2024
Firmware Version | 1.52
Point Format | Y
Horizontal Units | S
Horizontal Scale | 0.01
Sample Interval | 8e-07
Filter Frequency | 2e+08
Record Length | 125000
Gating | 0.0% to 100.0% |  | 0.0% to 100.0%
Probe Attenuation | 10 |  | 10
Vertical Units | V |  | V
Vertical Offset | 0 |  | 0
Vertical Scale | 1 |  | 1
Label
TIME | CH2 | CH2 Peak Detect | CH3 | CH3 Peak Detect
-3.00000e-02 | 0 | 0.08 | 0.02 | 0.06
-2.99992e-02 | 0 | -0.04 | 0.06 | -0.02
-2.99984e-02 | 0.04 | 0.08 | 0.06 | 0.06
-2.99976e-02 | 0 | -0.04 | 0.06 | -0.02
-2.99968e-02 | 0 | 0.08 | 0.02 | 0.06
-2.99960e-02 | 0 | -0.04 | 0.02 | -0.02
-2.99952e-02 | 0 | 0.08 | 0.02 | 0.06
-2.99944e-02 | 0 | -0.04 | 0.06 | -0.02
-2.99936e-02 | 0 | 0.08 | 0.02 | 0.06
-2.99928e-02 | 0 | -0.04 | 0.02 | -0.02
-2.99920e-02 | 0 | 0.08 | 0.02 | 0.06
-2.99912e-02 | 0 | -0.04 | 0.06 | -0.02
-2.99904e-02 | 0 | 0.08 | 0.06 | 0.06
-2.99896e-02 | 0 | -0.04 | 0.02 | -0.02
-2.99888e-02 | 0 | 0.08 | 0.02 | 0.06
-2.99880e-02 | 0.04 | -0.04 | 0.06 | -0.02
-2.99872e-02 | 0 | 0.08 | 0.06 | 0.06
-2.99864e-02 | 0 | -0.04 | 0.02 | -0.02
-2.99856e-02 | 0.04 | 0.08 | 0.02 | 0.1
-2.99848e-02 | 0 | -0.04 | 0.06 | -0.02
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

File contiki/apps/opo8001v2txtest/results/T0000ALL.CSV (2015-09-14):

Model | MSO2024
Firmware Version | 1.52
Point Format | Y
Horizontal Units | S
Horizontal Scale | 0.01
Sample Interval | 8e-07
Filter Frequency | 2e+08
Record Length | 125000
Gating | 0.0% to 100.0% |  | 0.0% to 100.0%
Probe Attenuation | 10 |  | 10
Vertical Units | V |  | V
Vertical Offset | 0 |  | 0
Vertical Scale | 1 |  | 1
Label
TIME | CH2 | CH2 Peak Detect | CH3 | CH3 Peak Detect
-3.00000e-02 | 0 | 0.08 | 3.3 | 3.38
-2.99992e-02 | 0 | -0.04 | 3.34 | 3.26
-2.99984e-02 | 0.04 | 0.08 | 3.34 | 3.38
-2.99976e-02 | 0.04 | -0.04 | 3.3 | 3.26
-2.99968e-02 | 0 | 0.08 | 3.3 | 3.38
-2.99960e-02 | 0.08 | -0.04 | 3.34 | 3.26
-2.99952e-02 | 0 | 0.08 | 3.34 | 3.38
-2.99944e-02 | 0 | -0.04 | 3.34 | 3.26
-2.99936e-02 | 0 | 0.08 | 3.3 | 3.38
-2.99928e-02 | 0 | -0.04 | 3.3 | 3.26
-2.99920e-02 | 0 | 0.08 | 3.34 | 3.38
-2.99912e-02 | 0 | -0.04 | 3.34 | 3.26
-2.99904e-02 | 0 | 0.08 | 3.34 | 3.38
-2.99896e-02 | 0.04 | -0.04 | 3.3 | 3.3
-2.99888e-02 | 0 | 0.08 | 3.3 | 3.38
-2.99880e-02 | 0.04 | -0.04 | 3.3 | 3.26
-2.99872e-02 | 0 | 0.08 | 3.34 | 3.38
-2.99864e-02 | -0.04 | -0.04 | 3.34 | 3.3
-2.99856e-02 | 0 | 0.08 | 3.34 | 3.38
-2.99848e-02 | 0 | -0.04 | 3.34 | 3.3
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

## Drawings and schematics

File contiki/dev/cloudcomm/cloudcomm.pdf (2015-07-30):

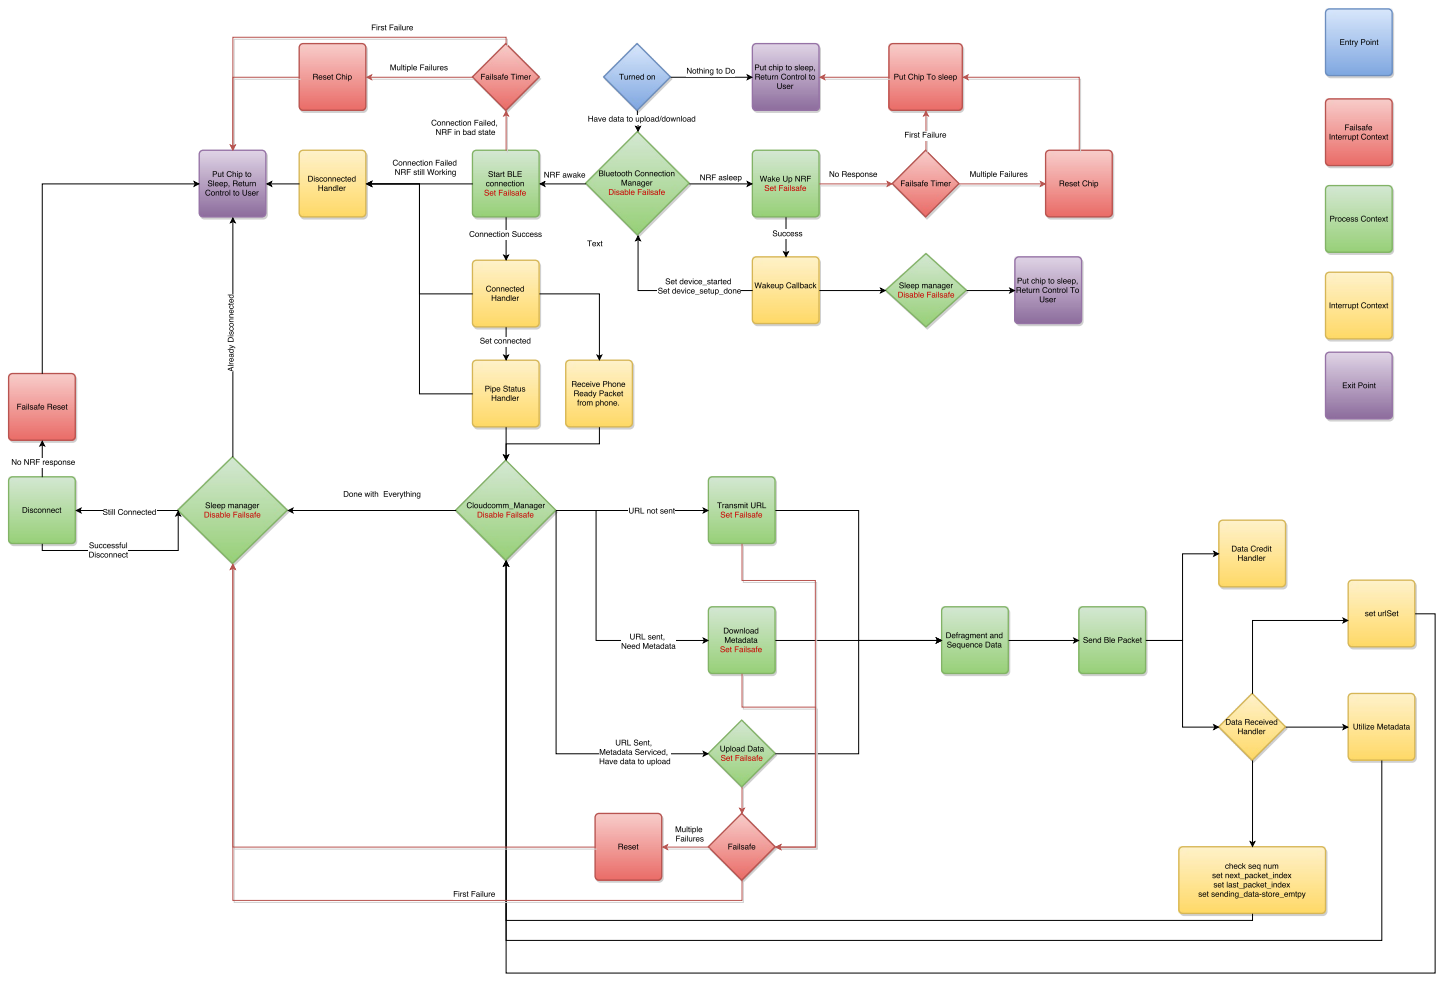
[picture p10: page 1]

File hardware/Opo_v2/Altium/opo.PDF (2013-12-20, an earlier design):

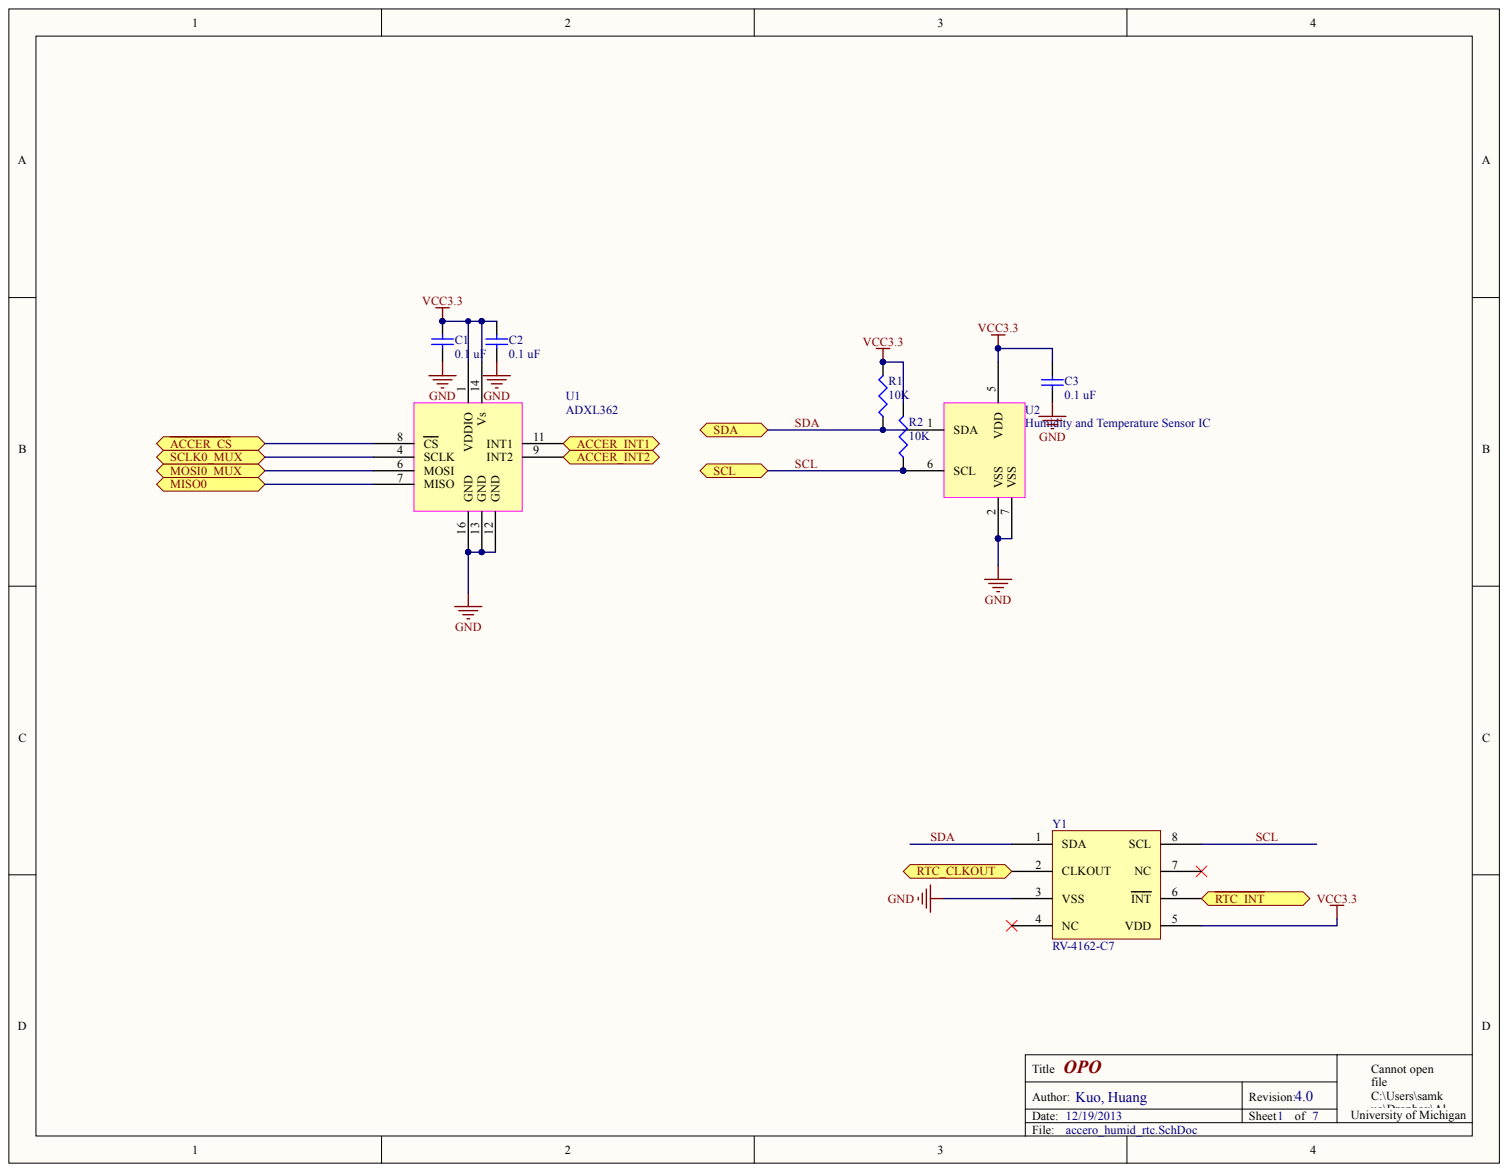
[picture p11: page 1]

GND 12 GND 13 Vs 14 GND 16

Humidity and Temperature Sensor IC
GND

Title OPO | Cannot open file C:\Users\samk uo\Dropbox\Al University of Michigan

Author: Kuo, Huang | Revision:
Date: | Sheet of

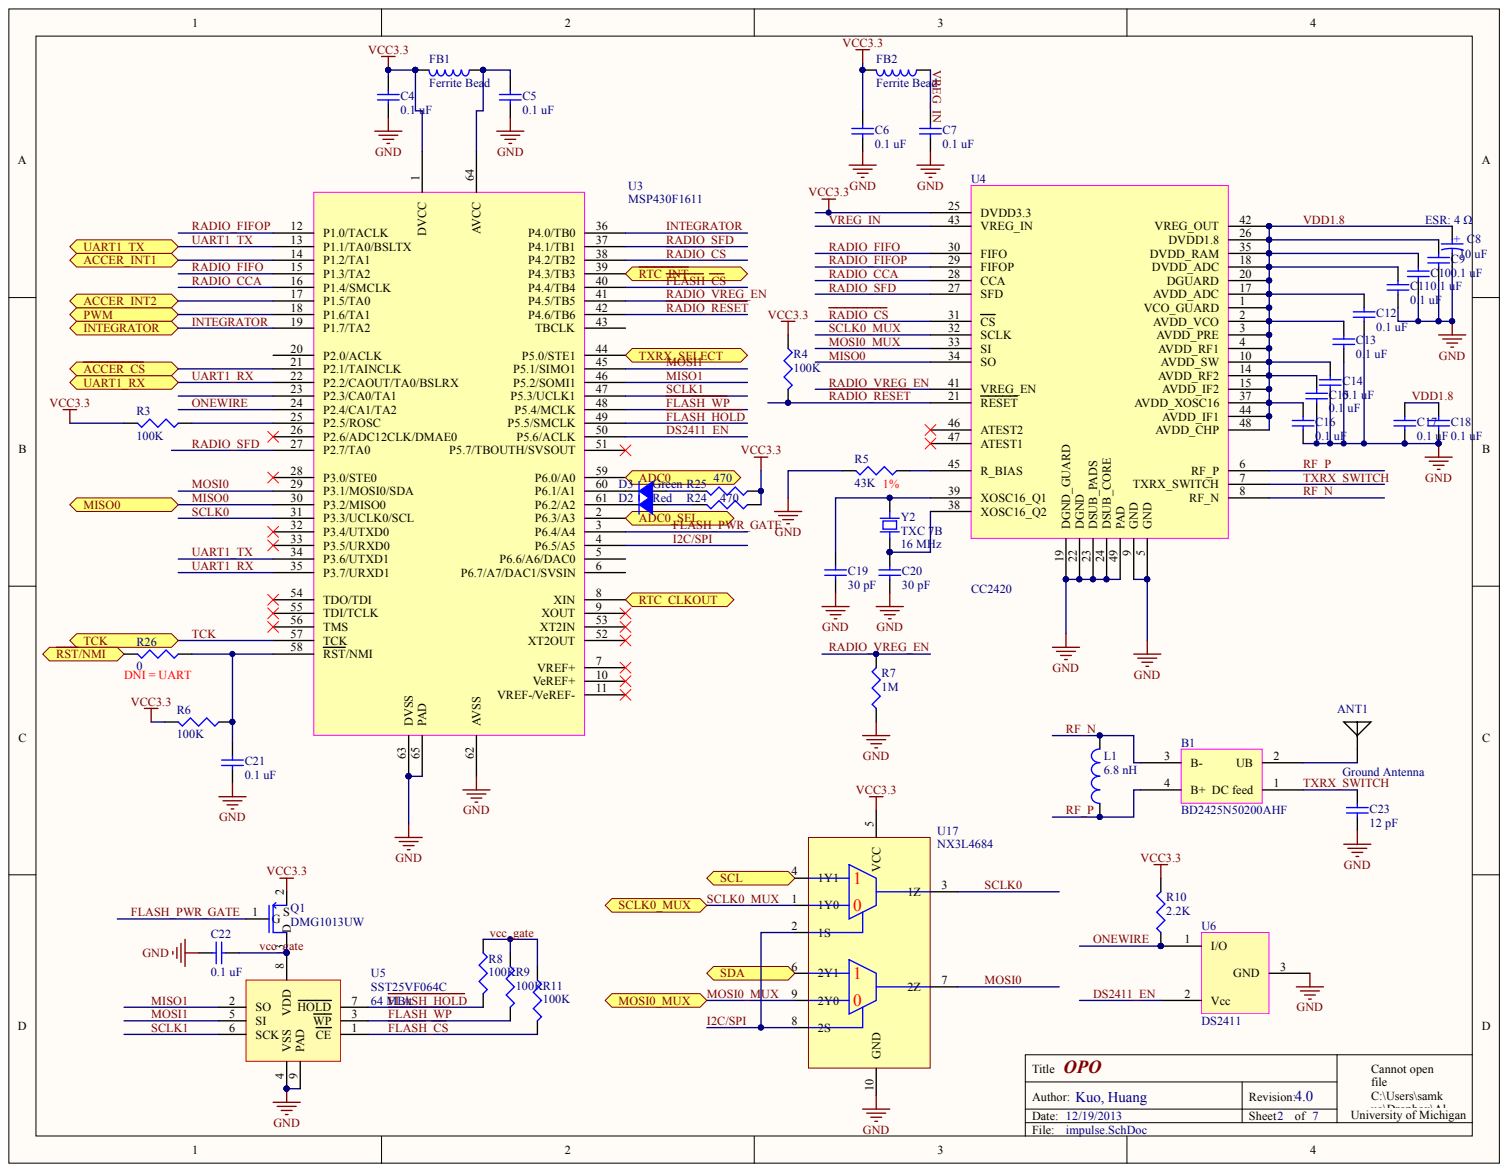
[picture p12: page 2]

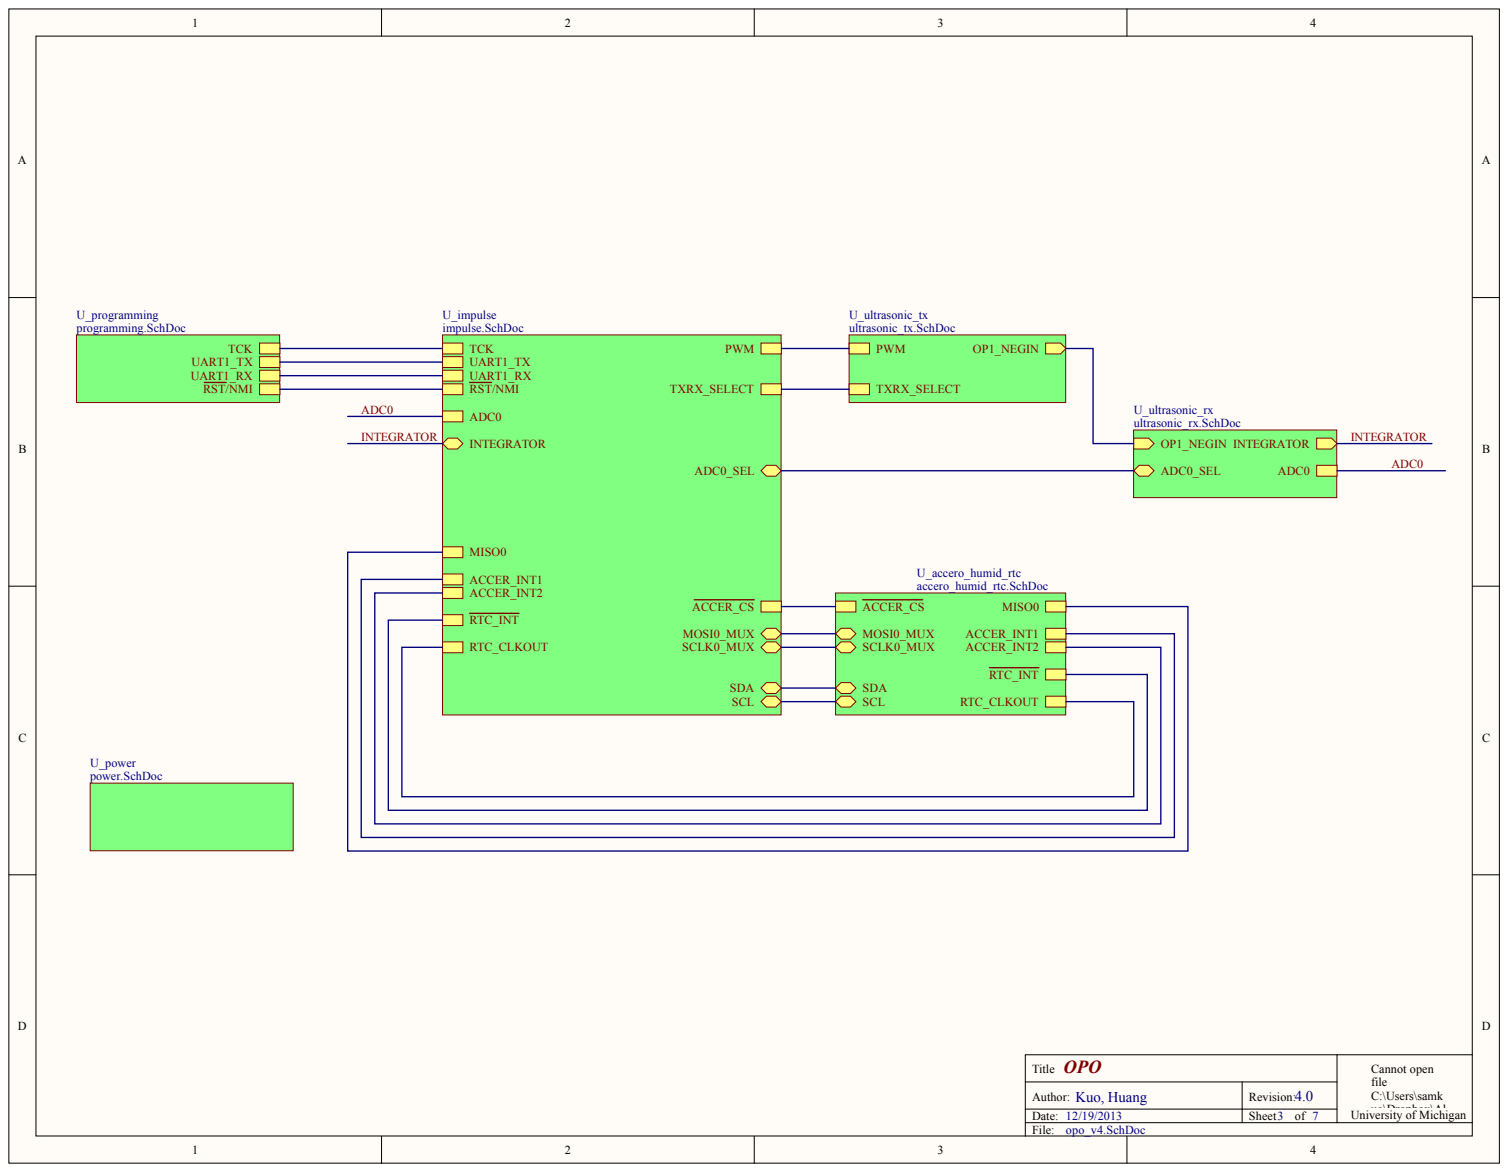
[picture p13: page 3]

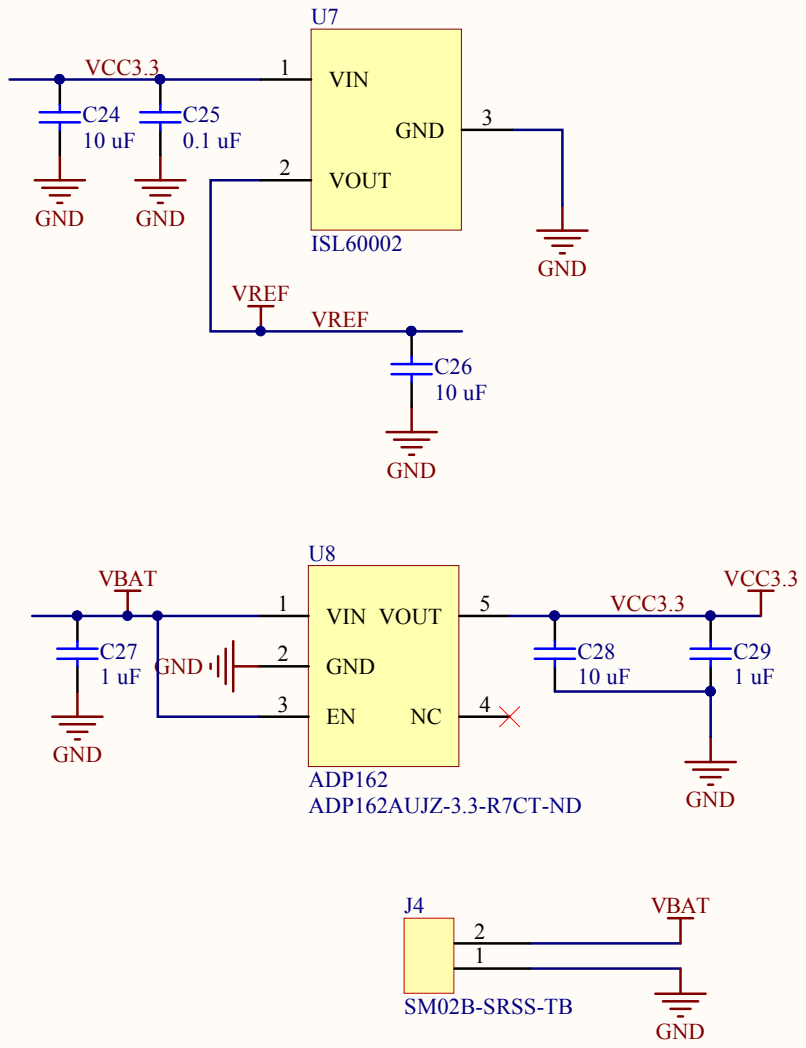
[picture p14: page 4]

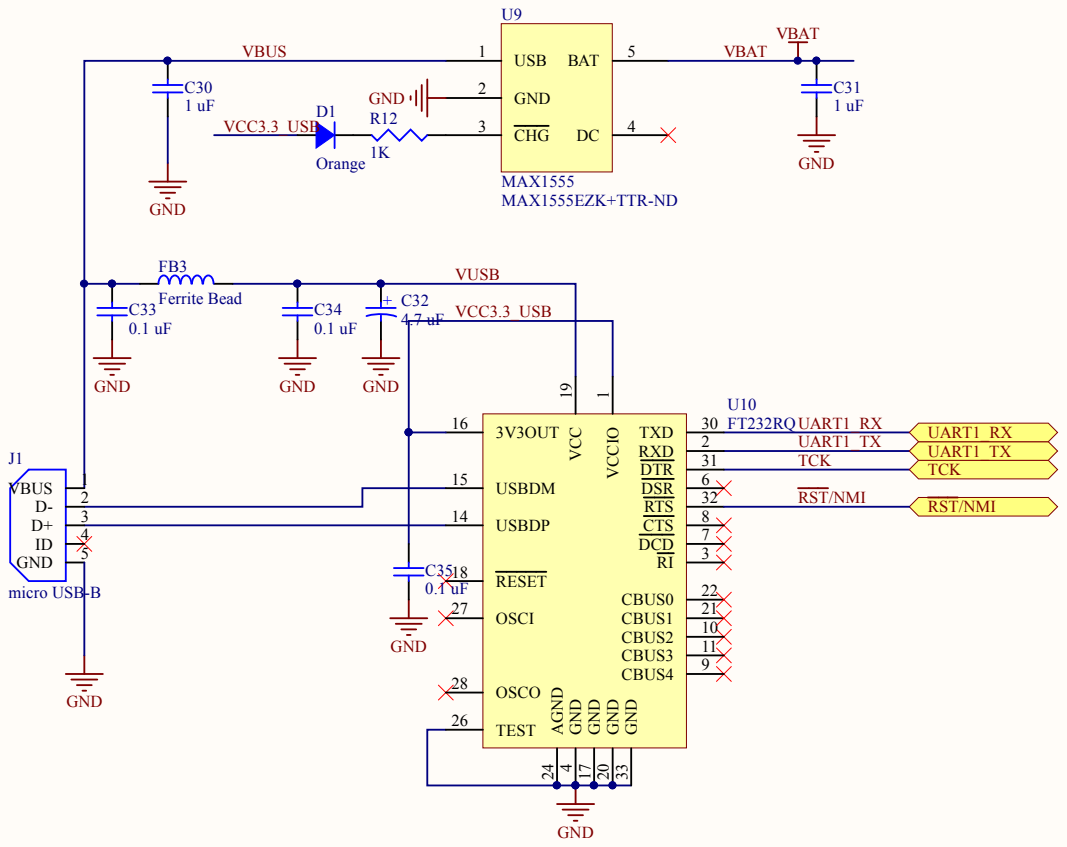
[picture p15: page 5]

RST/NMI

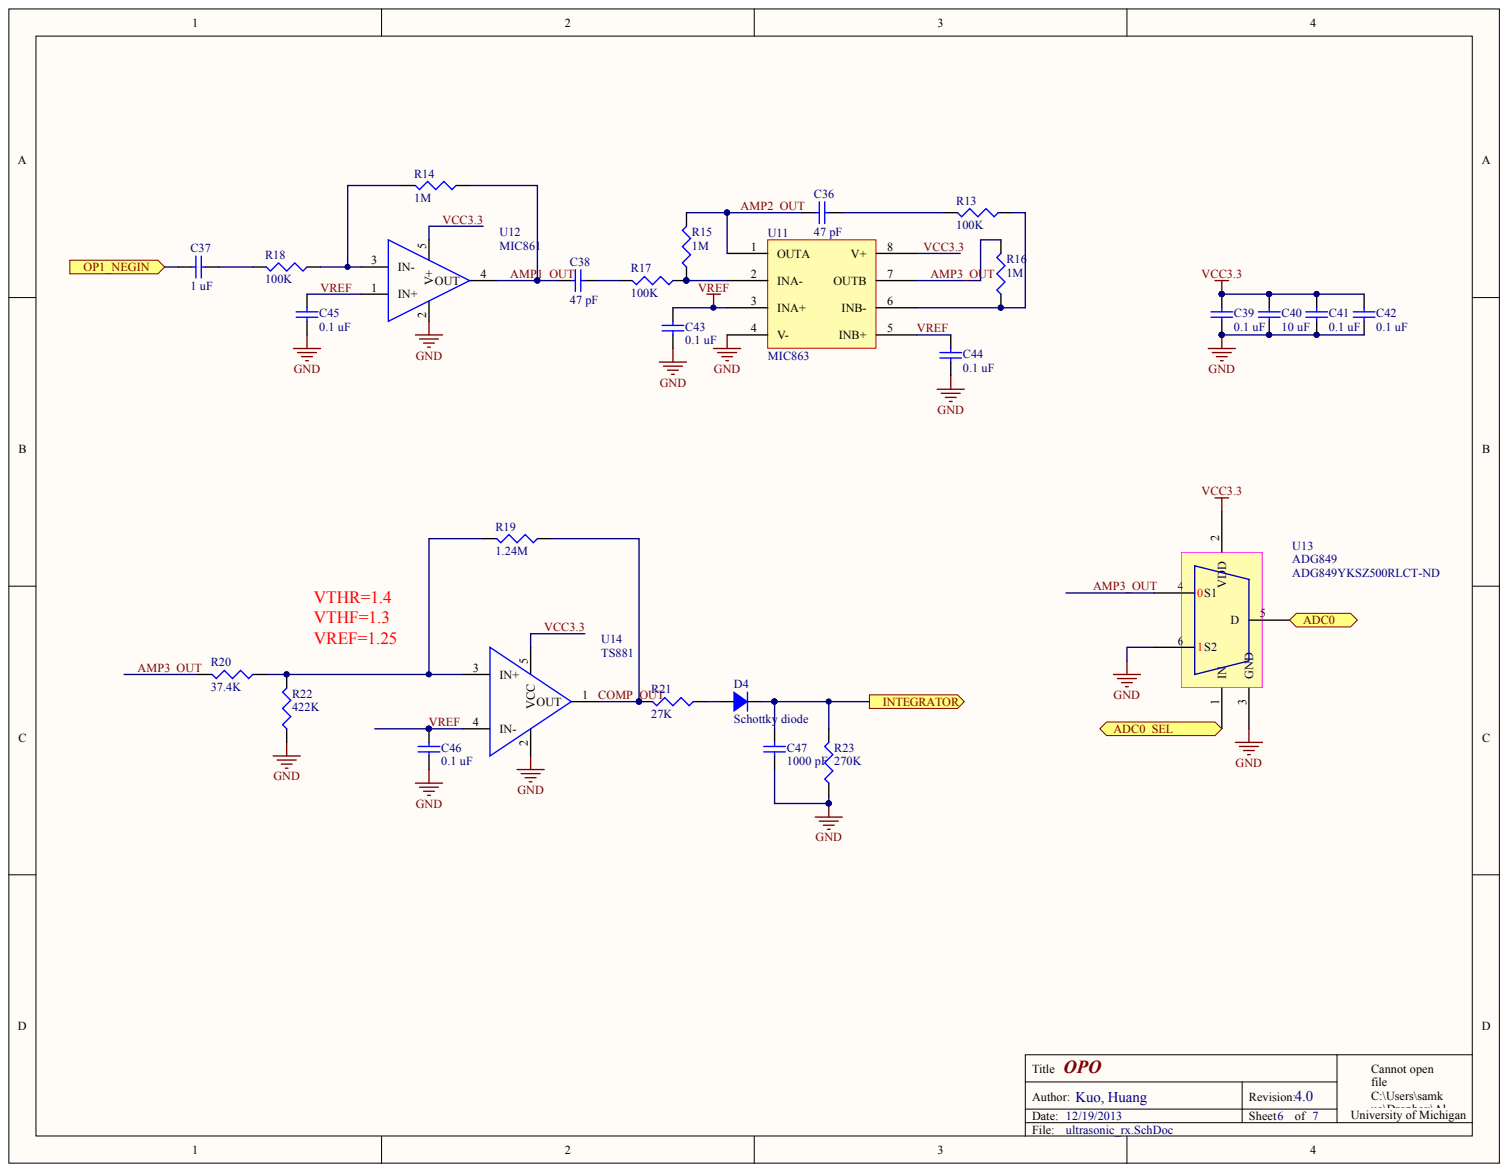
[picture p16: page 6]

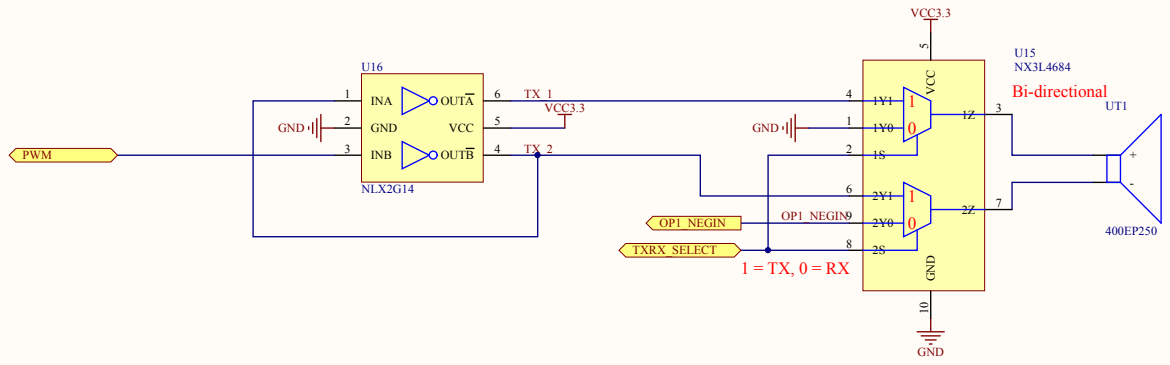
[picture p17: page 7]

Title OPO | Cannot open

Author: Kuo, Huang | Revision: Sheet of

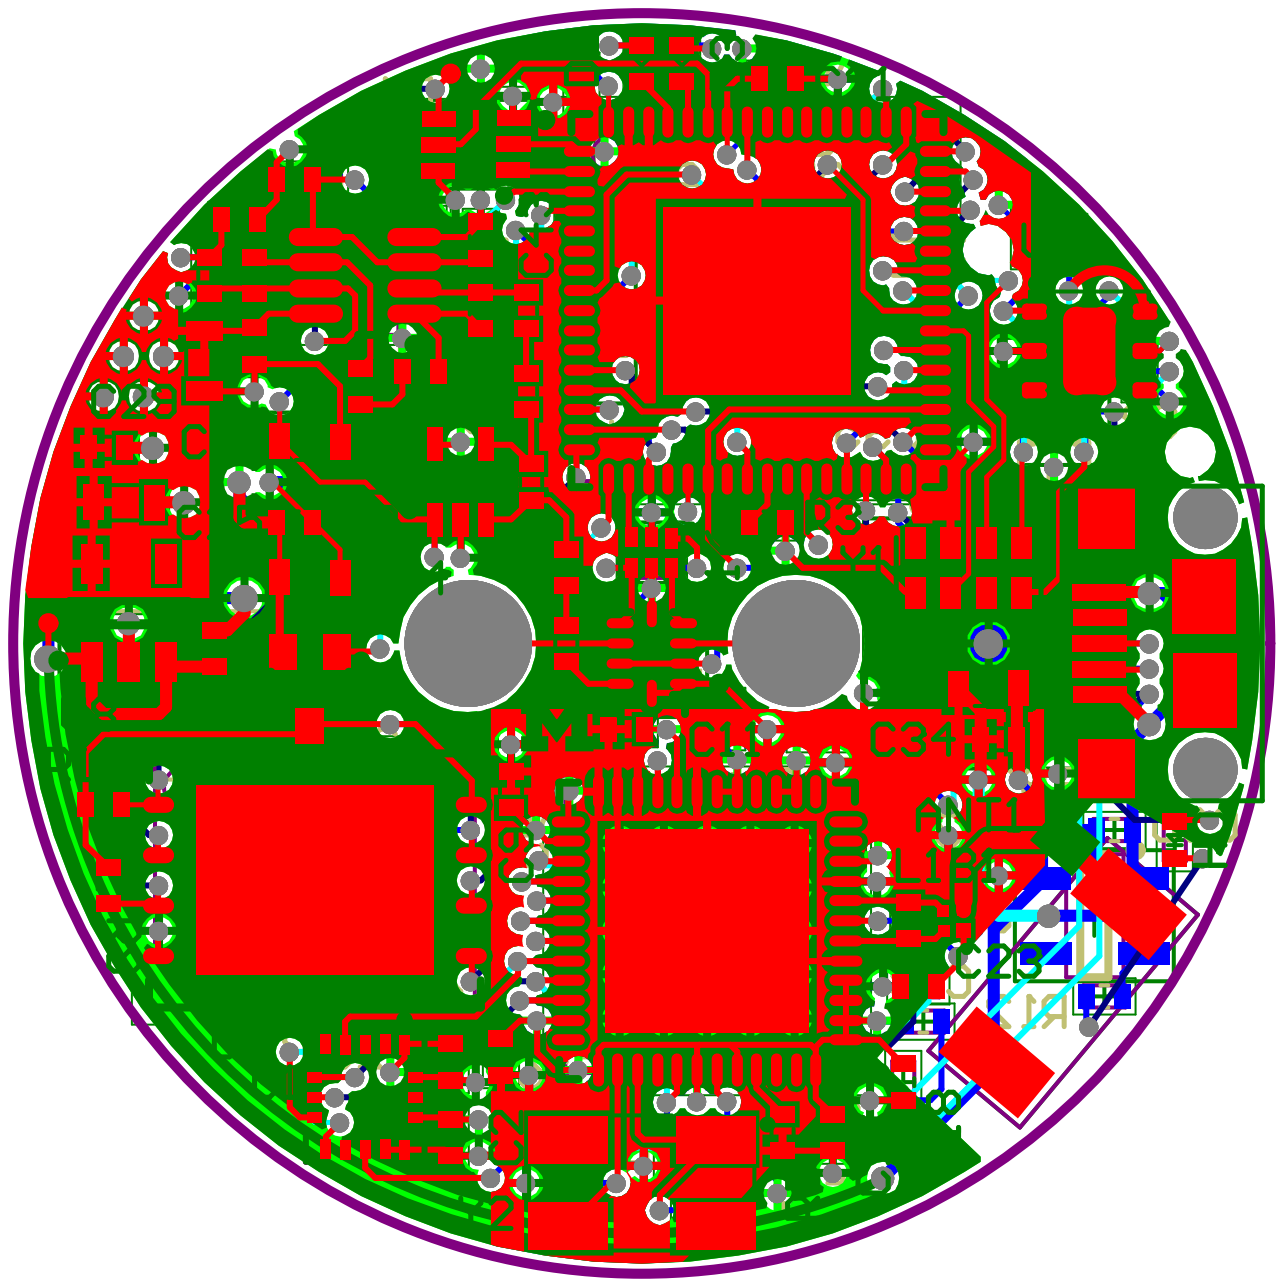
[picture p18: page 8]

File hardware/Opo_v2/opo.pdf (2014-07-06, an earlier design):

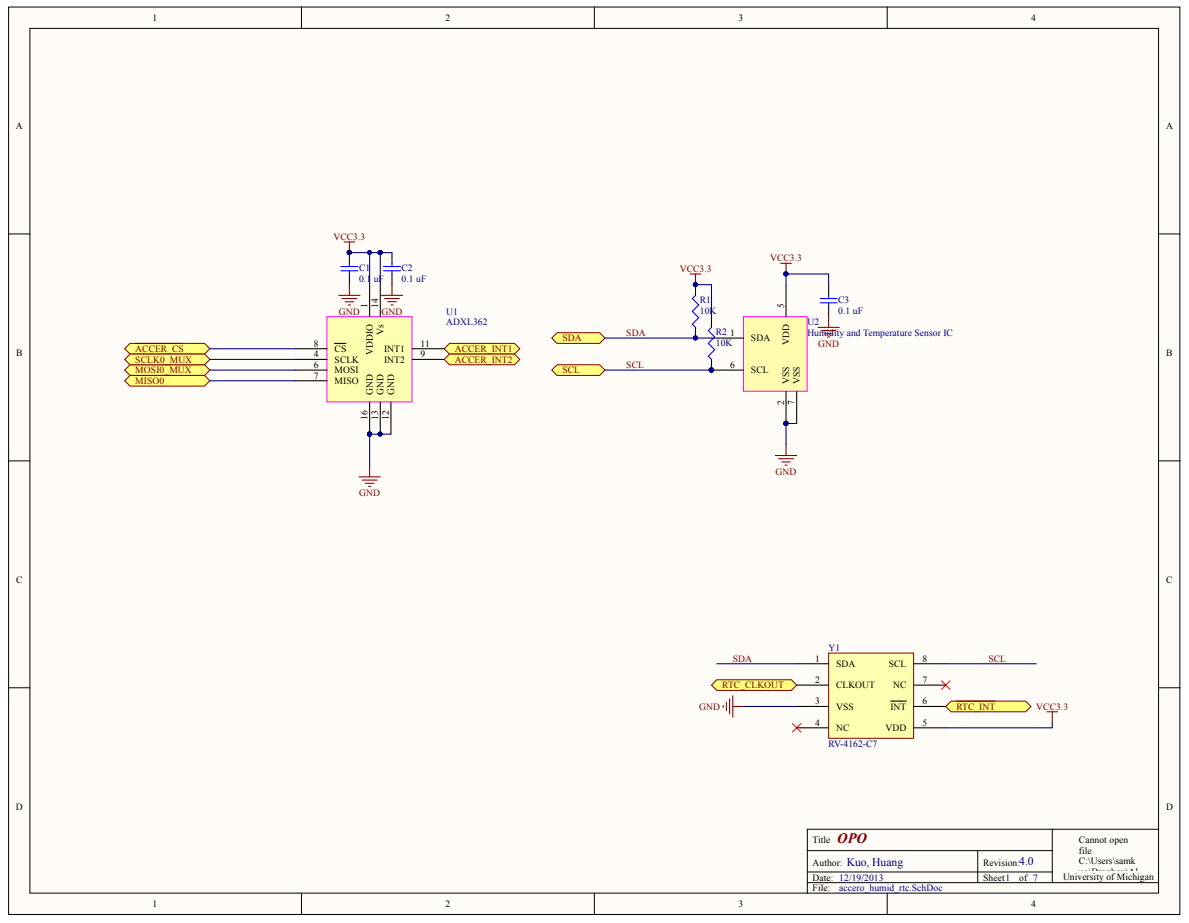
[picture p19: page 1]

GND 12 GND 13 Vs 14 GND 16

aPa Title | Cannot open file C:\Users\samk uo\Dropbox\Al University of Michigan

Author: Kuo, Huang | Revision:
Date: | Sheet of

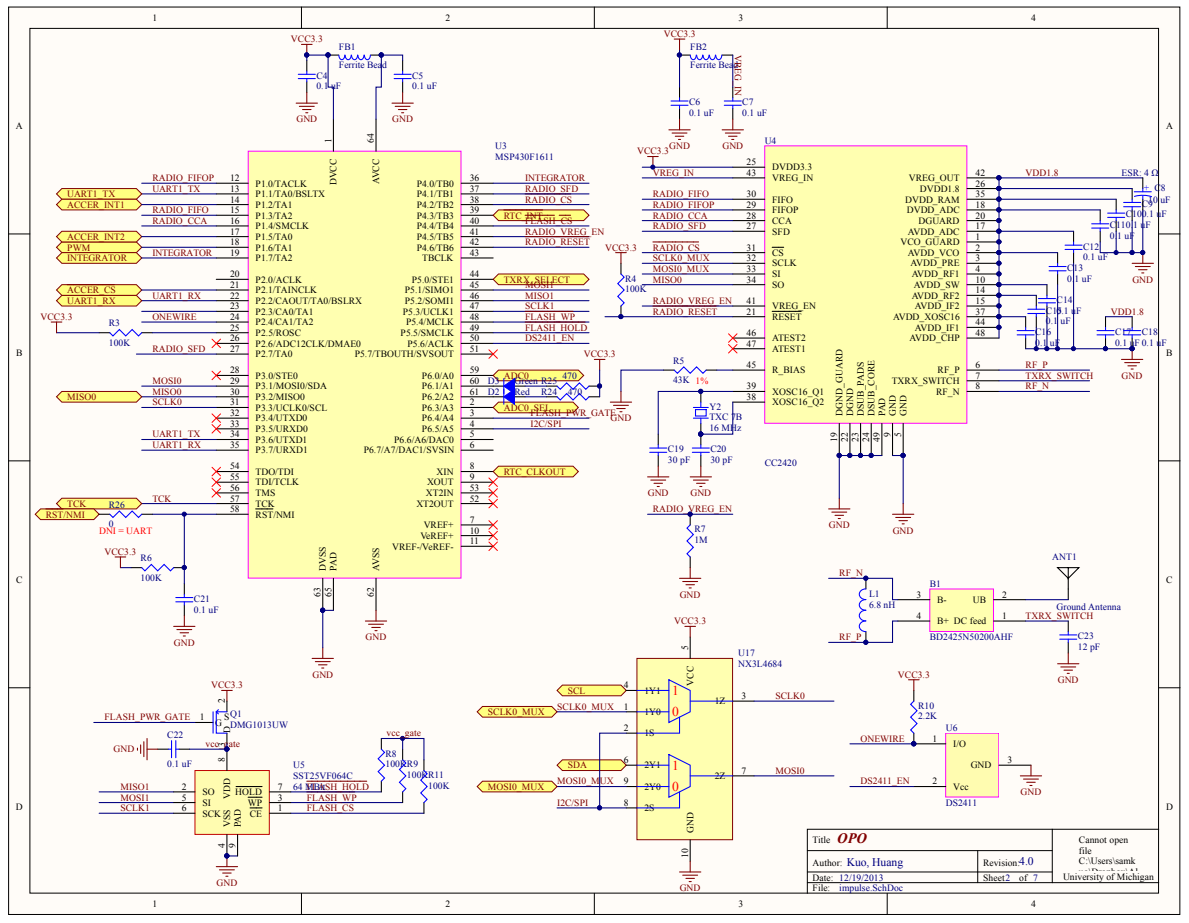
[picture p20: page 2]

XOSC16_Q2 38

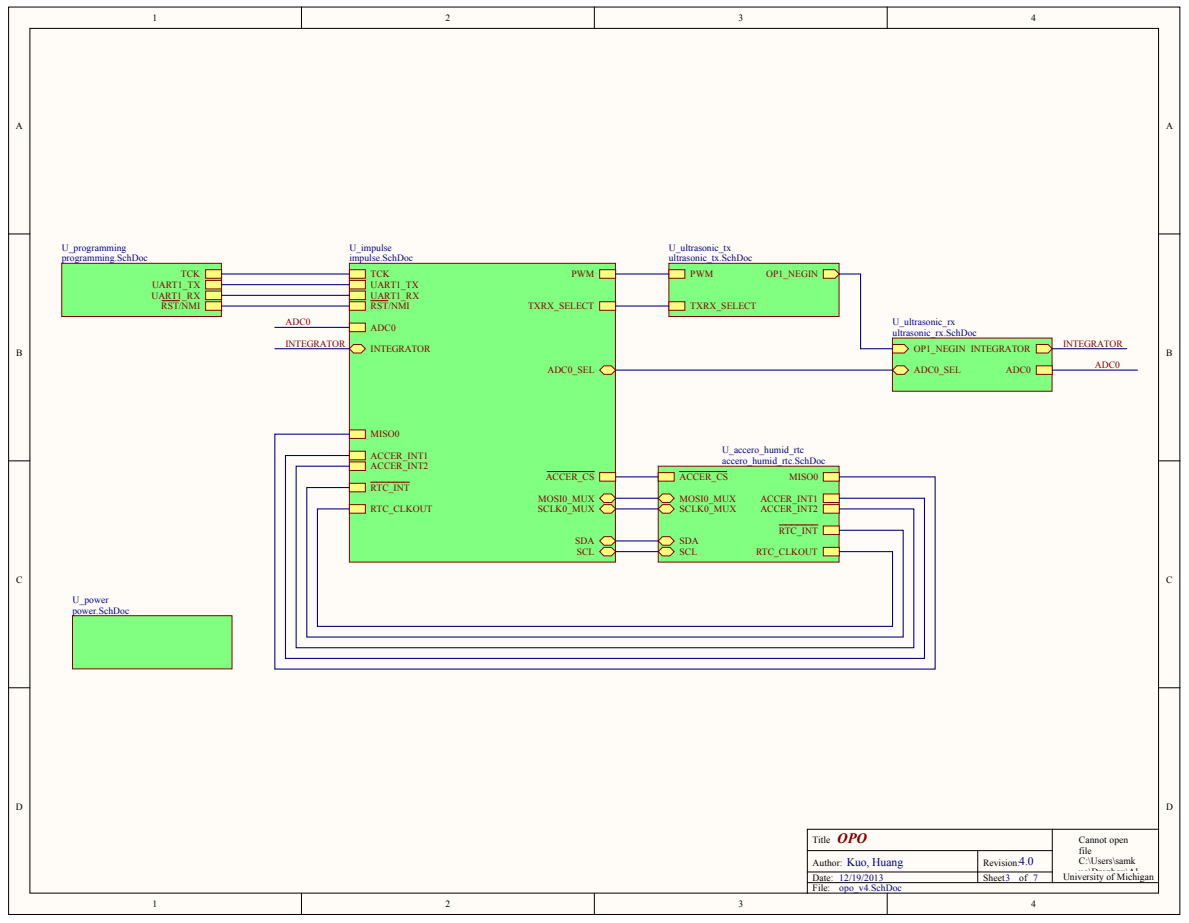
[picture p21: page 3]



RST/NMI




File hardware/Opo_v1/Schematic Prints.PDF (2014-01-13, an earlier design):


Ultrasonic Title | University of Michigan

Author: Kuo, Huang | Revision:
Date: | Sheet of



GND
SFD





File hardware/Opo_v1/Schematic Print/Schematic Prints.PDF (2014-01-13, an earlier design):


Ultrasonic Title | University of Michigan

Author: Kuo, Huang | Revision:
Date: | Sheet of



GND
SFD





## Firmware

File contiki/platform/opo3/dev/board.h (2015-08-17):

/*
 * Copyright (c) 2012, Texas Instruments Incorporated - http://www.ti.com/
 * All rights reserved.
 *
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
 * 3. Neither the name of the copyright holder nor the names of its
 *    contributors may be used to endorse or promote products derived
 *    from this software without specific prior written permission.
 *
 * THIS SOFTWARE IS PROVIDED BY THE COPYRIGHT HOLDERS AND CONTRIBUTORS
 * ``AS IS'' AND ANY EXPRESS OR IMPLIED WARRANTIES, INCLUDING, BUT NOT
 * LIMITED TO, THE IMPLIED WARRANTIES OF MERCHANTABILITY AND FITNESS
 * FOR A PARTICULAR PURPOSE ARE DISCLAIMED.  IN NO EVENT SHALL THE
 * COPYRIGHT HOLDER OR CONTRIBUTORS BE LIABLE FOR ANY DIRECT, INDIRECT,
 * INCIDENTAL, SPECIAL, EXEMPLARY, OR CONSEQUENTIAL DAMAGES
 * (INCLUDING, BUT NOT LIMITED TO, PROCUREMENT OF SUBSTITUTE GOODS OR
 * SERVICES; LOSS OF USE, DATA, OR PROFITS; OR BUSINESS INTERRUPTION)
 * HOWEVER CAUSED AND ON ANY THEORY OF LIABILITY, WHETHER IN CONTRACT,
 * STRICT LIABILITY, OR TORT (INCLUDING NEGLIGENCE OR OTHERWISE)
 * ARISING IN ANY WAY OUT OF THE USE OF THIS SOFTWARE, EVEN IF ADVISED
 * OF THE POSSIBILITY OF SUCH DAMAGE.
 */
/** \addtogroup cc2538
 * @{
 *
 * \defgroup cc2538-smartrf SmartRF06EB Peripherals
 *
 * Defines related to the SmartRF06EB
 *
 * This file provides connectivity information on LEDs, Buttons, UART and
 * other SmartRF peripherals
 *
 * Notably, PC0 is used to drive LED1 as well as the USB D+ pullup. Therefore
 * when USB is enabled, LED1 can not be driven by firmware.
 *
 * This file can be used as the basis to configure other platforms using the
 * cc2538 SoC.
 * @{
 *
 * \file
 * Header file with definitions related to the I/O connections on the TI
 * SmartRF06EB
 *
 * \note   Do not include this file directly. It gets included by contiki-conf
 *         after all relevant directives have been set.
 */
#ifndef BOARD_H_
#define BOARD_H_

#include "dev/gpio.h"
#include "dev/nvic.h"
/*---------------------------------------------------------------------------*/
/** \name LED configuration
 *
 *
 * @{
 */
/*---------------------------------------------------------------------------*/
/* Some files include leds.h before us, so we need to get rid of defaults in
 * leds.h before we provide correct definitions */
#undef LEDS_GREEN
#undef LEDS_YELLOW
#undef LEDS_RED
#undef LEDS_CONF_ALL

 /* No actual leds on board Using

 */

#define LEDS_YELLOW    128 /**< LED2 (Yellow) -> PC1 */
#define LEDS_GREEN     64 /**< LED3 (Green)  -> PC2 */
#define LEDS_ORANGE    32 /**< LED4 (Orange) -> PC3 */

#define LEDS_CONF_ALL 224

/* Notify various examples that we have LEDs */
#define PLATFORM_HAS_LEDS        0
/** @} */
/*---------------------------------------------------------------------------*/
/** \name UART configuration
 *
 * UART 0 configuration. This is how the bsl programs the board
 * @{
 */
#define UART0_RX_PORT            GPIO_A_NUM
#define UART0_RX_PIN             0

#define UART0_TX_PORT            GPIO_A_NUM
#define UART0_TX_PIN             1


/** @} */
/*---------------------------------------------------------------------------*/
/**
 * \name ADC configuration
 *
 * These values configure which CC2538 pins and ADC channels to use for the ADC
 * inputs.
 *
 * ADC inputs can only be on port A.
 * @{
 */
#define ADC_ALS_PWR_PORT         GPIO_A_NUM /**< ALS power GPIO control port */
#define ADC_ALS_PWR_PIN          7 /**< ALS power GPIO control pin */
#define ADC_ALS_OUT_PIN          6 /**< ALS output ADC input pin on port A */

/** @} */
/*---------------------------------------------------------------------------*/
/** \name Pin configs
 *
 * Opo4 pin configurations
 * @{
 */
// Software control pin masks
#define OPO_SFC_A_MASK	0xF8
#define OPO_SFC_B_MASK	0x97
#define OPO_SFC_C_MASK	0xF2
#define OPO_SFC_D_MASK	0xFF

// TX_RX sel pin info
#define OPO_TX_RX_SEL_PORT_BASE    GPIO_C_BASE
#define OPO_TX_RX_SEL_PIN_MASK	   0x02

// Integrator pin info
#define OPO_INT_PORT_BASE	GPIO_C_BASE
#define OPO_INT_PORT_NUM	GPIO_C_NUM
#define OPO_INT_PIN_MASK	0x80
#define OPO_INT_PIN_NUM		7
#define OPO_GPT_INT_PIN		23

// COMP1 pin info
#define OPO_COMP1_PORT_BASE	GPIO_C_BASE
#define OPO_COMP1_PORT_NUM	GPIO_C_NUM
#define OPO_COMP1_PIN_MASK	0x40
#define OPO_COMP1_PIN_NUM	6
#define OPO_GPT_COMP1_PIN	22

// COMP2 pin info
#define OPO_COMP2_PORT_BASE	GPIO_C_BASE
#define OPO_COMP2_PORT_NUM	GPIO_C_NUM
#define OPO_COMP2_PIN_MASK	0x20
#define OPO_COMP2_PIN_NUM	5
#define OPO_GPT_COMP2_PIN	21

// TX PWM Pins
#define OPO_PWM_PORT_BASE	GPIO_C_BASE
#define OPO_PWM_PORT_NUM	GPIO_C_NUM
#define OPO_PWM_PIN_MASK	0x01
#define OPO_PWM_PIN_NUM	    0

#define GPIO_A_OUTPUT_MASK 0xF8
#define GPIO_A_INPUT_MASK  0x00
#define GPIO_A_CLR_MASK    0xF8
#define GPIO_A_SET_MASK    0x00

#define GPIO_B_OUTPUT_MASK 0x13
#define GPIO_B_INPUT_MASK  0x84
#define GPIO_B_CLR_MASK	   0x00
#define GPIO_B_SET_MASK    0x13

#define GPIO_C_OUTPUT_MASK 0x03
#define GPIO_C_INPUT_MASK  0xe0
#define GPIO_C_CLR_MASK    0x03
#define GPIO_C_SET_MASK    0x00

#define GPIO_D_OUTPUT_MASK 0xff
#define GPIO_D_INPUT_MASK  0x00
#define GPIO_D_CLR_MASK    0xff
#define GPIO_D_SET_MASK    0x00

#define OPO_INT_NVIC       NVIC_INT_GPIO_PORT_C

//I2C Pins
#define I2C_SDA_PORT_NUM   GPIO_C_NUM
#define I2C_SDA_PIN_NUM	   3

#define I2C_SCL_PORT_NUM   GPIO_C_NUM
#define I2C_SCL_PIN_NUM	   2

// flash
#define SST25VF_CS_PORT_NUM					GPIO_B_NUM
#define SST25VF_CS_PIN_NUM					1
#define SST25VF_FLASH_POWER_PORT_BASE		GPIO_B_BASE
#define SST25VF_FLASH_POWER_PIN_MASK		0x01

/** @} */
/*---------------------------------------------------------------------------*/
/**
 * \name nrf8001 configuration
 *
 * These values configure which CC2538 pins are used to communicate with the
 * nrf8001.
 * @{
 */

#define RADIO_SELECT_PORT_BASE  GPIO_D_BASE
#define RADIO_SELECT_PIN_MASK   0x04
#define RADIO_SELECT_PORT		GPIO_D_NUM
#define RADIO_SELECT_PIN		2
#define RADIO_SELECT_VECTOR		NVIC_INT_GPIO_PORT_D

#define NRF8001_RDYN_PORT       GPIO_B_NUM
#define NRF8001_RDYN_PORT_BASE	GPIO_B_BASE
#define NRF8001_RDYN_PIN        7
#define NRF8001_RDYN_PIN_MASK	0x80
#define NRF8001_RDYN_VECTOR     NVIC_INT_GPIO_PORT_B

#define NRF8001_REQN_PORT 		GPIO_B_NUM
#define NRF8001_REQN_PORT_BASE	GPIO_B_BASE
#define NRF8001_REQN_PIN		4
#define NRF8001_REQN_PIN_MASK	0x10
#define NRF8001_REQN_VECTOR 	NVIC_INT_GPIO_PORT_B

#define NRF8001_ACTIVE_PORT		 GPIO_B_NUM
#define NRF8001_ACTIVE_PORT_BASE GPIO_B_BASE
#define NRF8001_ACTIVE_PIN		 2
#define NRF8001_ACTIVE_PIN_MASK	 0x04
#define NRF8001_ACTIVE_VECTOR	 NVIC_INT_GPIO_PORT_B
/** @} */

/*---------------------------------------------------------------------------*/
/**
 * \name SPI configuration
 *
 * These values configure which CC2538 pins to use for the SPI lines.
 * @{
 */
#define SPI_CLK_PORT             GPIO_B_NUM
#define SPI_CLK_PIN              3
#define SPI_MOSI_PORT            GPIO_B_NUM
#define SPI_MOSI_PIN             5
#define SPI_MISO_PORT            GPIO_B_NUM
#define SPI_MISO_PIN             6
/** @} */
/*---------------------------------------------------------------------------*/
/**
 * \name Device string used on startup
 * @{
 */
#define BOARD_STRING "Opo3"
/** @} */

#endif /* BOARD_H_ */

/**
 * @}
 * @}
 */

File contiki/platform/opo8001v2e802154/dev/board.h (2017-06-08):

/*
 * Copyright (c) 2012, Texas Instruments Incorporated - http://www.ti.com/
 * All rights reserved.
 *
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
 * 3. Neither the name of the copyright holder nor the names of its
 *    contributors may be used to endorse or promote products derived
 *    from this software without specific prior written permission.
 *
 * THIS SOFTWARE IS PROVIDED BY THE COPYRIGHT HOLDERS AND CONTRIBUTORS
 * ``AS IS'' AND ANY EXPRESS OR IMPLIED WARRANTIES, INCLUDING, BUT NOT
 * LIMITED TO, THE IMPLIED WARRANTIES OF MERCHANTABILITY AND FITNESS
 * FOR A PARTICULAR PURPOSE ARE DISCLAIMED.  IN NO EVENT SHALL THE
 * COPYRIGHT HOLDER OR CONTRIBUTORS BE LIABLE FOR ANY DIRECT, INDIRECT,
 * INCIDENTAL, SPECIAL, EXEMPLARY, OR CONSEQUENTIAL DAMAGES
 * (INCLUDING, BUT NOT LIMITED TO, PROCUREMENT OF SUBSTITUTE GOODS OR
 * SERVICES; LOSS OF USE, DATA, OR PROFITS; OR BUSINESS INTERRUPTION)
 * HOWEVER CAUSED AND ON ANY THEORY OF LIABILITY, WHETHER IN CONTRACT,
 * STRICT LIABILITY, OR TORT (INCLUDING NEGLIGENCE OR OTHERWISE)
 * ARISING IN ANY WAY OUT OF THE USE OF THIS SOFTWARE, EVEN IF ADVISED
 * OF THE POSSIBILITY OF SUCH DAMAGE.
 */
/** \addtogroup cc2538
 * @{
 *
 * Defines related to the Opo4 Platform
 *
 * This file provides connectivity information on LEDs, UL frontends, etc
 *
 * This file can be used as the basis to configure other platforms using the
 * cc2538 SoC.
 * @{
 *
 * \file
 * Header file with definitions related to I/O connections
 *
 * \note   Do not include this file directly. It gets included by contiki-conf
 *         after all relevant directives have been set.
 */
#ifndef BOARD_H_
#define BOARD_H_

#include "dev/gpio.h"
#include "dev/nvic.h"
#include "dev/gptimer.h"
#include "dev/ioc.h"
/*---------------------------------------------------------------------------*/
/** \name LED configuration
 *
 *
 * @{
 */
/*---------------------------------------------------------------------------*/
/* Some files include leds.h before us, so we need to get rid of defaults in
 * leds.h before we provide correct definitions */
#undef LEDS_RED
#undef LEDS_GREEN
#undef LEDS_BLUE
#undef LEDS_CONF_ALL

 /* No actual leds on board Using

 */

#define LEDS_RED    0x01 /* PB0 */
#define LEDS_GREEN  0x40 /* PD6 */
#define LEDS_BLUE   0x02 /* PB1 */

#define LEDS_CONF_ALL 0x51

/* Notify various examples that we have LEDs */
#define PLATFORM_HAS_LEDS        1
/** @} */
/*---------------------------------------------------------------------------*/
/** \name UART configuration
 *
 * UART 0 configuration. This is how the bsl programs the board
 * @{
 */
#define UART0_RX_PORT            GPIO_A_NUM
#define UART0_RX_PIN             0

#define UART0_TX_PORT            GPIO_A_NUM
#define UART0_TX_PIN             1

/** @} */
/*---------------------------------------------------------------------------*/
/** \name Pin configs
 *
 * Opo4 pin configurations
 * @{
 */

// TX_RX sel pin info: PC7
#define OPO_TX_RX_SEL_PORT_BASE    GPIO_C_BASE
#define OPO_TX_RX_SEL_PIN_MASK	   0x80

// COMP1 pin info
#define OPO_COMP1_PORT_BASE	GPIO_D_BASE
#define OPO_COMP1_PORT_NUM	GPIO_D_NUM
#define OPO_COMP1_PIN_MASK	0x80
#define OPO_COMP1_PIN_NUM	7

#define OPO_COMP1_NVIC     NVIC_INT_GPIO_PORT_D
#define OPO_RX_NVIC        OPO_COMP1_NVIC

#define OPO_RX_PORT_BASE   OPO_COMP1_PORT_BASE
#define OPO_RX_PORT_NUM    OPO_COMP1_PORT_NUM
#define OPO_RX_PIN_MASK    OPO_COMP1_PIN_MASK
#define OPO_RX_PIN_NUM     OPO_COMP1_PIN_NUM

// TX PWM Pins
#define OPO_PWM_PORT_BASE	GPIO_B_BASE
#define OPO_PWM_PORT_NUM	GPIO_B_NUM
#define OPO_PWM_PIN_MASK	0x08
#define OPO_PWM_PIN_NUM	    3

// Plug in detect
#define PLUG_DETECT_PORT_BASE	GPIO_A_BASE
#define PLUG_DETECT_PORT_NUM	GPIO_A_NUM
#define PLUG_DETECT_PIN_MASK	0x20
#define PLUG_DETECT_PIN_NUM	    5

// Initial input/output masks
#define GPIO_A_OUTPUT_MASK 0xdf
#define GPIO_A_INPUT_MASK  0x20
#define GPIO_A_CLR_MASK    0xff
#define GPIO_A_SET_MASK    0x00 // I think UART line should be clear..?

#define GPIO_B_OUTPUT_MASK 0xff
#define GPIO_B_INPUT_MASK  0x00
#define GPIO_B_CLR_MASK	   0xfc
#define GPIO_B_SET_MASK    0x03

#define GPIO_C_OUTPUT_MASK 0xdb
#define GPIO_C_INPUT_MASK  0x24
#define GPIO_C_CLR_MASK    0xa4
#define GPIO_C_SET_MASK    0x5b

#define GPIO_D_OUTPUT_MASK 0x7b
#define GPIO_D_INPUT_MASK  0x84
#define GPIO_D_CLR_MASK    0xb6
#define GPIO_D_SET_MASK    0x49

/** @} */
/*---------------------------------------------------------------------------*/
/** \name Pin configs
 *
 * Opo4 tx and rx timer config
 * @{
 */
#define OPO_PWM_GPTIMER			GPTIMER_1
#define OPO_PWM_GPSUBTIMER		GPTIMER_SUBTIMER_A

#define OPO_COMP1_GPTIMER		GPTIMER_2
#define OPO_COMP1_GPSUBTIMER	GPTIMER_SUBTIMER_A
#define OPO_COMP1_GPT_OCP		IOC_GPT2OCP1
#define OPO_COMP1_GPT_BASE		GPTIMER_2_BASE
#define OPO_COMP1_GPT_TV		GPTIMER_TAV
#define OPO_COMP1_OFINT			GPTIMER_ICR_TATOCINT // overflow interrupt
#define OPO_COMP1_CAPINT		GPTIMER_ICR_CAECINT  // capture interrupt
#define OPO_COMP1_GPT_NVIC		NVIC_INT_GPTIMER_2A

#define OPO_COMP2_GPTIMER		GPTIMER_2
#define OPO_COMP2_GPSUBTIMER	GPTIMER_SUBTIMER_B
#define OPO_COMP2_GPT_OCP		IOC_GPT2OCP2
#define OPO_COMP2_GPT_BASE		GPTIMER_2_BASE
#define OPO_COMP2_GPT_TV		GPTIMER_TBV

#define OPO_INT_GPTIMER			GPTIMER_1
#define OPO_INT_GPSUBTIMER		GPTIMER_SUBTIMER_B
#define OPO_INT_GPT_OCP			IOC_GPT1OCP2

/** @} */
/*---------------------------------------------------------------------------*/
/**
 * \name ADC configuration
 *
 * These values configure which CC2538 pins and ADC channels to use for the ADC
 * inputs.
 *
 * ADC inputs can only be on port A.
 * @{
 */
#define ADC_ALS_PWR_PORT         GPIO_A_NUM /**< ALS power GPIO control port */
#define ADC_ALS_PWR_PIN          4 /**< ALS power GPIO control pin */
#define ADC_ALS_OUT_PIN          5 /**< ALS output ADC input pin on port A */
/** @} */
/** @} */
/*---------------------------------------------------------------------------*/
/**
 * \name nrf8001 configuration
 *
 * These values configure which CC2538 pins are used to communicate with the
 * nrf8001.
 * @{
 */

#define NRF8001_RDYN_PORT       	GPIO_C_NUM
#define NRF8001_RDYN_PORT_BASE		GPIO_C_BASE
#define NRF8001_RDYN_PIN        	2
#define NRF8001_RDYN_PIN_MASK		0x04
#define NRF8001_RDYN_VECTOR     	NVIC_INT_GPIO_PORT_C

#define NRF8001_REQN_PORT 			GPIO_D_NUM
#define NRF8001_REQN_PORT_BASE		GPIO_D_BASE
#define NRF8001_REQN_PIN			0
#define NRF8001_REQN_PIN_MASK		0x01
#define NRF8001_REQN_VECTOR 		NVIC_INT_GPIO_PORT_D

#define NRF8001_ACTIVE_PORT		 	GPIO_A_NUM
#define NRF8001_ACTIVE_PORT_BASE 	GPIO_A_BASE
#define NRF8001_ACTIVE_PIN		 	3
#define NRF8001_ACTIVE_PIN_MASK	 	0x08
#define NRF8001_ACTIVE_VECTOR	 	NVIC_INT_GPIO_PORT_A

#define NRF8001_RESET_PORT			GPIO_D_NUM
#define NRF8001_RESET_PORT_BASE		GPIO_D_BASE
#define NRF8001_RESET_PIN			3
#define NRF8001_RESET_PIN_MASK		0x08
#define NRF8001_RESET_VECTOR		NVIC_INT_GPIO_PORT_D


/** @} */

/*---------------------------------------------------------------------------*/
/**
 * \name Flash Storage configuration
 *
 * These values configure which CC2538 pins are used to communicate with the
 * SST25VF flash chip.
 * @{
 */

#define SST25VF_CS_PORT_NUM					GPIO_D_NUM
#define SST25VF_CS_PIN_NUM					4
#define SST25VF_CS_PORT_BASE                GPIO_D_BASE
#define SST25VF_CS_PIN_MASK                 0x10

#define SST25VF_FLASH_POWER_PORT_BASE		GPIO_C_BASE
#define SST25VF_FLASH_POWER_PIN_MASK		0x08

#define SST25VF_FLASH_RESET_PORT_BASE		GPIO_C_BASE
#define SST25VF_FLASH_RESET_PIN_MASK		0x40

/** @} */

#define ADXL362_CS_PORT_NUM GPIO_C_NUM
#define ADXL362_CS_PIN_NUM  4

#define ADXL362_INTTWO_PORT_BASE GPIO_C_BASE
#define ADXL362_INTTWO_PIN_MASK  0x20
#define ADXL362_INTTWO_PORT_NUM  GPIO_C_NUM
#define ADXL362_INTTWO_PIN_NUM   5
#define ADXL362_INTTWO_NVIC      NVIC_INT_GPIO_PORT_C
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

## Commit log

2013-12-12 tinoys shit
    [Node_Ids.csv]
2013-12-19 changed default msp430 pin settings
2013-12-20 starting new visual demo
    [Node_Ids.csv]
2014-01-07 removing printfs, minor stuff
2014-01-08 hardware info
    [BOM_opo.xlsx, opo_v4.GBL, opo_v4.GBO, opo_v4.GBP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]
2014-01-10 wiring for flash chip Hpl
2014-01-13 hardare files for older opo stuff
    [Bill of Materials-ultrasonic_ranging_v2.xls, ultrasonic_v3_2.GBL, ultrasonic_v3_2.GBO, ultrasonic_v3_2.GBS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]
2014-01-13 renaming opo versions
    [BOM_mod.xlsx, BOM_mod_2013.05.01.xlsx, BOM_mod_packed.xlsx, BOM_opo.xlsx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]
2014-01-14 altium files
    [accero_humid_rtc.SchDoc, impulse.SchDoc, opo.PrjPcb, opo_v4.PcbDoc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]
2014-01-17 Opo flash drivers. Will be switching to asyncronous interface since I dont want to busywait for milliseconds
2014-01-29 starting humidity sensor driver
2014-01-30 humidity sensor shit
2014-01-30 humidity sensor drivers
2014-01-30 test app for humidity sensor
2014-02-07 added leds for debugging
2014-02-08 app to store shit for original opo
    [Node_Ids.csv]
2014-02-19 rough pricing for 1k of these
    [BOM_opo_1000.xlsx]
2014-02-19 removing debug leds
2014-02-20 adding in support for flashreader time calibration
2014-03-09 leds changes
2014-03-14 removed printf for speeeed
2014-03-14 readding print
2014-03-26 modfiying for current flash driver
2014-03-26 Update list_opo script to print more useful information
    Passing any argument will flip to 'verbose' mode / the old behavoir
2014-03-26 Improve duplicate printout
2014-03-27 flowchart for opo2 operation
2014-04-09 wiring to OpoC i2cswitch
2014-05-07 cleanup first
    [BOM_opo.xlsx, BOM_opo_1000.xlsx, accero_humid_rtc.SchDoc, impulse.SchDoc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]
2014-05-07 updated files
    [Bill of Materials-opo.xls, Bill of Materials-opo4.1.xls, accero_humid_rtc.SchDoc, impulse.SchDoc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]
2014-07-06 general altium libs, split between ics and rlc parts
    [opo_general.PcbLib, opo_general.SchLib, opo_general.csv, rlc.PcbLib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]
2014-07-06 opo ble debug board
    [Bill of Materials-opo_v3.xls, Bill of Materials-opo_v3.xlsx, accero_humid_rtc.SchDoc, bluetooth.SchDoc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]
2014-07-06 board overview
2014-07-06 gerber files, boms, etc for board
    [Bill of Materials-opo4.1.xls, opo_v4.1.GBL, opo_v4.1.GBO, opo_v4.1.GBP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]
2014-07-18 minor changes. App currently tests for device started event
2014-07-18 opo3 conf stuff. Merging a lot of atum and cc2538dk stuff to make spi (from atum) and sensor events (from cc2538dk) stuff work
2014-07-18 currently testing: device boot and putting in test mode
2014-07-18 adding test and echo function prototypes
2014-07-20 removing pull up resistor for RDYN pin. doesn't look like it needs one
2014-07-22 adding defines in for delayed boot based on pin interrupt
2014-07-22 added leds in for showing status of test program
2014-07-23 switching from testing nrf8001 test functions to testing actual bluetooth stuff. Currently broadcasts advertisements
2014-07-27 adding in bond prototype
2014-09-14 discovery, etimer operates at 128 Hz, switching to rtimer
2014-10-01 new opo board. BLE enabled, meant to be worn
    [bluetooth.SchDoc, mcu.SchDoc, opo4.PcbDoc, opo4.PrjPCB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]
2014-10-13 opo3 altium stuff
    [accero_humid_rtc.SchDoc, bluetooth.SchDoc, mcu.SchDoc, opo_v3.0.PcbDoc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]
2014-10-13 general libraries for opo parts
    [opo_general.PcbLib, opo_general.SchLib, rlc.PcbLib, rlc.SchLib]
2014-10-13 cleaning up altium stuff for opo3
    [Bill of Materials-opo_v3.xls, Bill of Materials-opo_v3.xlsx, opo_v3.0.GBL, opo_v3.0.GBO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]
2014-10-13 opo4 altium stuff
    [Bill of Materials-opo4 (William Huang's conflicted copy 2014-10-07).xlsx, Bill of Materials-opo4.xls, Bill of Materials-opo4.xlsx, mcu.SchDoc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]
2014-10-13 cleaning up opo 3 platform. pins now set during init stage
2014-10-20 checkpoint. fixing shit now
    [opo4.PcbDoc]
2014-10-20 opo v3
    [Bill of Materials-opo_v3.xlsx, accero_humid_rtc.SchDoc, bluetooth.SchDoc, mcu.SchDoc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]
2014-10-20 fixing errors in opo v4
    [mcu.SchDoc, opo4.PcbDoc, opo4.PrjPCB, opo_general.PcbLib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]
2014-10-27 switching nrf8001 drivers from using sensors_changed to callbacks
2014-11-17 minor modifications + a lot of cleanup
    [Bill of Materials-opo4 (William Huang's conflicted copy 2014-10-07).xlsx, Bill of Materials-opo_v3.xlsx, accero_humid_rtc.SchDoc, bluetooth.SchDoc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]
2014-11-17 changed nrf8001 drivers to use callback functions instead of contiki SENSORS CHANGED shit
2014-11-17 removing old, sensors changed based nrf8001 drivers
2014-11-17 remove sensors changed shit
2014-11-17 toggle blue led on successful tx
2014-12-08 hardware bug fixes
    [mcu.SchDoc, opo4.PcbDoc]
2015-01-30 hardware bom and gerb updates
    [Bill of Materials-opo4.xls, Bill of Materials-opo4.xlsx, bluetooth.SchDoc, mcu.SchDoc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]
2015-01-31 saving case
    design still in progress
    [case_bottom.SLDPRT, case_top.SLDPRT, case_top_2.SLDPRT, jewel.SLDASM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]
2015-01-31 changes to case
    [case_bottom.SLDPRT, case_top_2.SLDPRT, jewel.SLDASM, transducer.SLDPRT]
2015-02-06 power test app with results
2015-02-09 cloudcomm init now enables power up interrupts from the nrf8001 and takes care of nrf8001 sleep
2015-02-26 Application for using phones as BLE IoT gateways. Currently supports connections, receiving packets, and acking them on the applicatoin level
2015-03-23 YET ANOTHER VERSION OF OPO.
    [Bill of Materials-opo4.xlsx, bluetooth.SchDoc, mcu.SchDoc, opo4.GBL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]
2015-03-23 oops fixed an error.
    [opo8001.PcbDoc]
2015-03-25 some fixes thanks to ye-sheng
    [mcu.SchDoc, opo8001.PcbDoc, opo8001.PrjPCB, programmer_charger.SchDoc]
2015-03-26 cleanning up some shit
    [Bill of Materials-opo4.xlsx, opo4.GBL, opo4.GBO, opo4.GBP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]
2015-03-26 shit sent for assembly
    [opo8001.PcbDoc, opo8001.PrjPCB]
2015-03-26 gerber + drill file sent for manufacturing
2015-04-06 outjob file and minor schematic fix
    [mcu.SchDoc, opo8001.PcbDoc, opo8001.PrjPCB]
2015-07-21 Lots of cloducomm code cleanup, and a graphical control flow diagram now.
    Functionally, main change is everything is now failsafe timered, and if there are multiple failures we just hard reset the flash chip.
2015-07-23 more altium parts
    [opo_general.PcbLib, opo_general.SchLib, rlc.SchLib]
2015-07-23 oops, forgot the h file for my printf over 802.15.4
2015-07-23 older version of some of my contiki conf files. just in case
2015-07-23 less broken version of opo
    [bluetooth.SchDoc, mcu.SchDoc, opo8001.PcbDoc, opo8001.PrjPCB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]
2015-08-04 opo ble with no ftdi chip
    [Bill of Materials-opo8001.xlsx, bluetooth.SchDoc, mcu.SchDoc, opo8001.PcbDoc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]
2015-08-17 lots of hardware cleanup
    [bluetooth.SchDoc, mcu.SchDoc, opo4.PcbDoc, opo4.PrjPCB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]
2015-08-17 opo case
    [case_top_2.ipt]
2015-09-01 pin state fixes
2015-09-10 null power test
2015-09-14 simple opo rx test
    [T0000ALL.CSV]
2015-09-14 A simple opo transmission test
    [T0000ALL.CSV]
2015-09-14 Added the ability to disable the clkout pin. Also made it to that when the clock isn't in use, we drive the i2c lines high to reduce power usage
2015-09-14 A lot of cleanup/documentation Fixed a case where cc doesn't handle perpetual reconnects on a nrf8001 restart utilize new millisecond vtimers
2015-11-12 added more debug info and made an led blink
2015-11-12 various power configs and shit
2016-03-15 added more debug info printed over rf
2016-08-17 hardware files
    [bluetooth.SchDoc, mcu.SchDoc, opo8001.PcbDoc, opo8001.PrjPCB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]
2017-06-08 adding back in contiki stuff? at some point I think I hid it for a paper submission
    [T0000ALL.CSV]
2017-08-03 Update README.md
    Added LED blinking description.
